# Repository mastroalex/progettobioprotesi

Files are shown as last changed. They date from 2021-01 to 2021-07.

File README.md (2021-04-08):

# progettobioprotesi
The following report aims to accurately explain what were the logical steps that led to the creation of the prototype of a rehabilitation system for the ankle. The patent provided to us was a source of inspiration for the number of components and how they relate to each other. For the shape of these we decided to deviate from the original design, opting for small variations of a mainly stylistic nature. The details and reasons for these changes will be presented below.
In this report there is also a careful study of the materials and how these can affect the functioning of the project or how they can instead bring great advantages.

---

La seguente relazione ha come obiettivo di spiegare accuratamente quali sono stati i passaggi logici che hanno portato alla creazione del prototipo di un sistema riabilitativo per la caviglia. Il brevetto fornitoci è stata fonte di ispirazione per il numero di componenti e come queste si relazionassero tra di loro. Per la forma di queste abbiamo deciso di deviare dal design originale, optando per piccole variazioni di natura principalmente stilistica. I dettagli e i motivi di queste modifiche saranno presentati più avanti.
In questa relazione è presente anche un attento studio ai materiali e come questi possano inficiare il funzionamento del progetto o come possano invece portare grandi vantaggi.

---

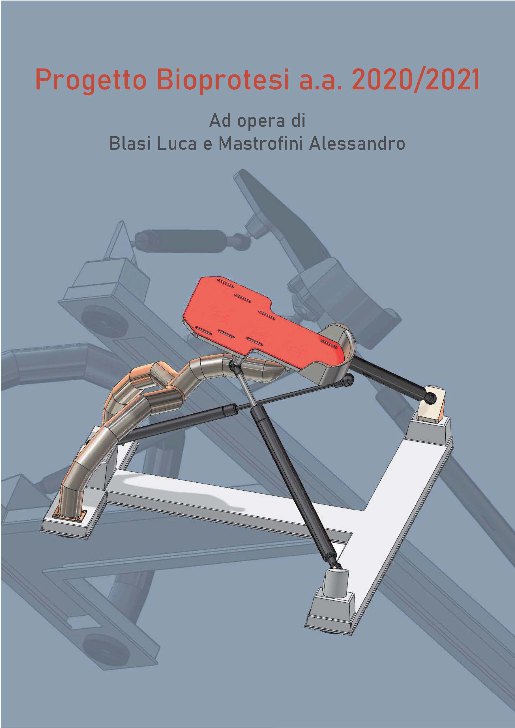
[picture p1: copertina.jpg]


## Indice 

  * [Introduzione](#introduzione)
  * [Misure e valutazioni iniziali](#misure-e-valutazioni-iniziali)
    + [Cinematica della caviglia](#cinematica-della-caviglia)
    + [Misure strumentali](#misure-strumentali)
    + [Valutazioni al calcolatore](#valutazioni-al-calcolatore)
  * [Progetto](#progetto)
    + [Considerazioni iniziali](#considerazioni-iniziali)
    + [Scelta dei pistoni](#scelta-dei-pistoni)
    + [Scelta delle dimensioni e disegno dei componenti](#scelta-delle-dimensioni-e-disegno-dei-componenti)
    + [Il giunto sferico](#il-giunto-sferico)
    + [La pedana](#la-pedana)
    + [Il braccio di supporto](#il-braccio-di-supporto)
    + [La base](#la-base)
    + [Il cappuccio (piastrina di accoppiamento)](#il-cappuccio--piastrina-di-accoppiamento-)
    + [I pistoni](#i-pistoni)
    + [Materiali](#materiali)
    + [Altri componenti](#altri-componenti)
  * [Simulazioni](#simulazioni)
    + [Flessione](#flessione)
    + [Rotazione](#rotazione)
    + [Eversione/inversione](#eversione-inversione)
    + [Pitch + roll](#pitch---roll)
    + [Un’ulteriore conferma](#un-ulteriore-conferma)
    + [Condizione di riposo](#condizione-di-riposo)
  * [Dettagli](#dettagli)
  * [Conclusioni e possibili sviluppi](#conclusioni-e-possibili-sviluppi)
  * [Materiale supplementare](#materiale-supplementare)
  * [Opere citate](#opere-citate)
  * [Indice delle figure](#indice-delle-figure)
  * [Figure extra](#figure-extra)

## Introduzione 

La seguente relazione ha come obiettivo di spiegare accuratamente quali sono stati i passaggi logici che hanno portato alla creazione del prototipo di un sistema riabilitativo per la caviglia. Il brevetto fornitoci è stata fonte di ispirazione per il numero di componenti e come queste si relazionassero tra di loro. Per la forma di queste abbiamo deciso di deviare dal design originale, optando per piccole variazioni di natura principalmente stilistica. I dettagli e i motivi di queste modifiche saranno presentati più avanti.
In questa relazione è presente anche un attento studio ai materiali e come questi possano inficiare il funzionamento del progetto o come possano invece portare grandi vantaggi.
Il brevetto US 6,277,057B1 [1] fornisce una attenta descrizione del dispositivo che riassumeremo brevemente al fine di facilitare la lettura e comprensione della relazione.
Il dispositivo si compone principalmente delle seguenti parti:
- base
- braccio di supporto 
- pedana
- apparati resistivi

La base è la componente che fornisce stabilità al dispositivo e durante l’utilizzo sarà poggiata a terra. Collegato alla base abbiamo il braccio di supporto che si estende ortogonalmente per il primo tratto dalla base per poi portarsi verso il centro di questa, ad una determinata quota dalla base. All’estremità di questo troveremo una estensione che la collega a una sfera. Quest’ultimo elemento sarà essenziale per la composizione del “ball and socket joint” che permetterà alla pedana di ruotare per creare i movimenti cardine della riabilitazione.
Sulla suddetta pedana il paziente potrà poggiare il piede la cui caviglia necessita esercizio. Al di sotto di questa pedana troviamo il socket, una cavità che permette di accogliere la sfera citata prima. Questa cavità coprirà la sfera in modo tale da bloccare le traslazioni relative tra braccio di supporto e pedana. Sarà modellata in modo tale da permettere la rotazione della sfera entro certi limiti, aspetto che discuteremo successivamente.
Questo giunto appena descritto quindi collega il braccio di supporto e la pedana, permettendone le rotazioni relative. Considerato come il braccio di supporto sia ancorato alla base sarà quindi possibile immaginare la pedana sollevata da terra e libera di ruotare.

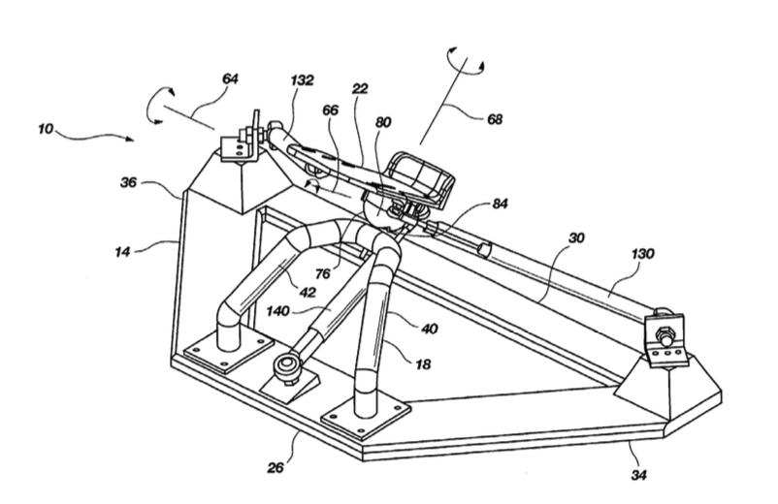
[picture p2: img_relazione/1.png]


> **Fig. 1** - Fig. 1 – Immagine tratta direttamente dal brevetto US 6,227,057B1 [1]

Alla stessa pedana sono anche collegati quelli che il brevetto definisce come “resistive means”, ossia congegni capaci di opporre resistenza ad allungamento ed accorciamento. Questi congegni collegheranno direttamente la pedana alla base, con l’obiettivo di opporre resistenza, elemento fondamentale della riabilitazione.
Facendo riferimento alle normative ISO 20957-1 per le attrezzature da allenamento e la normativa ISO 14971 per la gestione del rischio per i dispostivi medicali abbiamo cercato di focalizzaci su un dispositivo semplice e con bassi costi di produzione e manutenzione che garantisse un certo comfort all’utilizzatore ma che al contempo fosse stabile durante il movimento e riducesse al minimo la possibilità di ulteriori infortuni. Essendo un dispositivo di riabilitazione deve garantire il corretto movimento articolare in tutte le direzioni e permettere un certo lavoro tale da favorire la rigenerazione corretta dei tessuti danneggiati ma allo stesso tempo deve limitare movimenti troppo bruschi e bloccare il movimento ai limiti articolari prevenendo ulteriori infortuni [2, 3, 4, 5].
Il dispositivo, per come è stato strutturato, prevede sia un carico isometrico ai limiti articolari sia un intenso esercizio propriocettivo volto ad ottimizzare il recupero della cinematica articolare.
Una particolare attenzione è stata dedicata anche alla scelta di un materiale che risultasse quanto più possibile anallergico e resistente alla corrosione data da un eventuale pulizia e sanificazione intensiva nel caso venisse utilizzato da più utenti, come all’interno di uno studio medico.

## Misure e valutazioni iniziali 

Una prima valutazione è stata fatta cercando in letteratura un modello semplice ma sufficientemente accurato che descrivesse la cinematica della caviglia in un modo che risultasse utile allo sviluppo del progetto. 

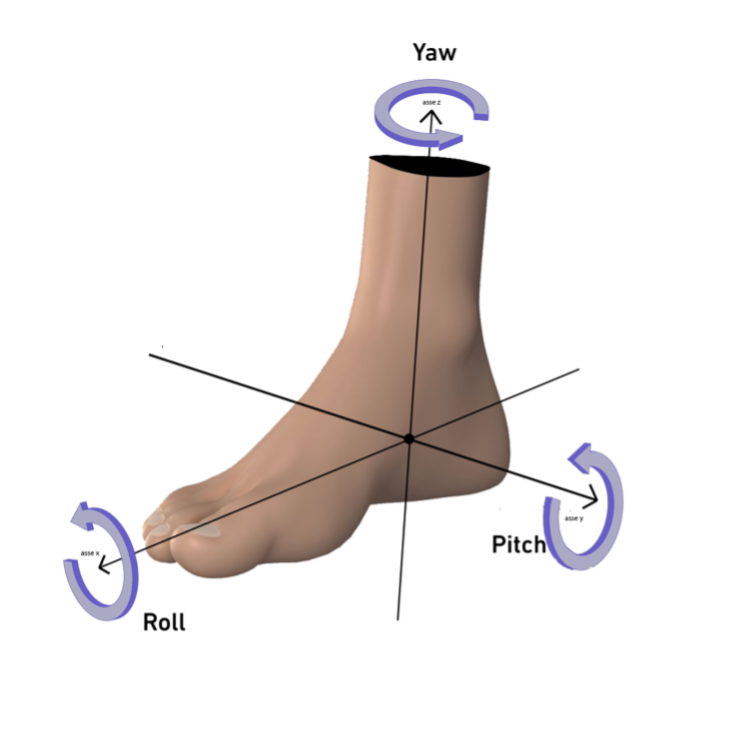
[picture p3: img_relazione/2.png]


> **Fig. 2** - Sistema di riferimento considerato per il piede destro. Le tre rotazioni sono state classificate rispettivamente come yaw (Y) intorno l’asse z, roll (R) intorno l’asse x e pitch (P) intorno l’asse y.

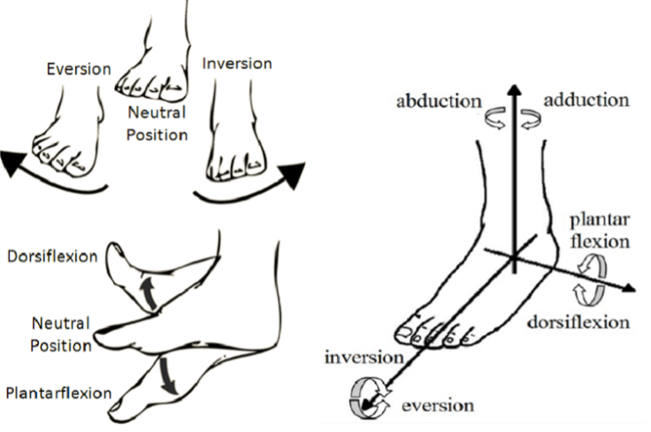
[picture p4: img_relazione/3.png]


> **Fig. 3** - Sono raffigurati i normali movimenti di rotazione dell’articolazione della caviglia. L’eversione e l’inversione indicato come (R) ovvero la rotazione intorno l’asse x. La flessione plantare e dorsale indicato come (P) ovvero la rotazione intorno l’asse y. L’abduzione e l’adduzione spesso indicate come rotazione mediale e laterale indicate come (Y) ovvero la rotazione intorno l’asse z.

### Cinematica della caviglia 

La caviglia unisce il segmento della gamba con il piede. È formata dall’unione di tre ossa: tibia, fibula e talo e da numerosi legamenti che le tengono unite e le stabilizzano. Come le altre articolazioni della gamba è responsabile del supporto del peso dell’intero corpo e richiede un’ottima rigidezza tendinea e muscolare. 

Ci sono 28 ossa e 26 articolazioni in ogni piede e caviglia che permettono un insieme di diversi movimenti e l’assorbimento della forza peso nel caso stazionario e di forze molto più intense nel caso di corsa o di impatti violenti come nei salti. Gran parte delle articolazioni sono delle anfiartrosi con legamenti molto rigidi che permettono soltanto movimenti minimi tuttavia conferiscono al piede una notevole flessibilità elastica e consentono di distribuire i carichi di compressione agenti in tensioni elastiche sui legamenti di una struttura complessivamente leggera. L’escursione del piede è variabile da persona a persona e con l’età ed è bene sottolineare il fatto che l’escursione complessiva data sia dall’articolazione talocrurale che subtalare è notevolmente maggiore della somma delle escursioni di ogni singola articolazione la ragione di tale fenomeno risiede nei legamenti il cui grado di tensione può essere aumentato o ridotto a seconda dei movimenti delle strutture adiacenti. L’articolazione talocrurale è formata dalla tibia, dalla fibula (o perone) e dalla troclea dell’astragalo e dai numerosi legamenti e capsula articolare necessari alla stabilizzazione. È un’articolazione a cerniera il cui asse decorre trasversalmente attraverso la forchetta malleolare e la troclea dell’astragalo. 

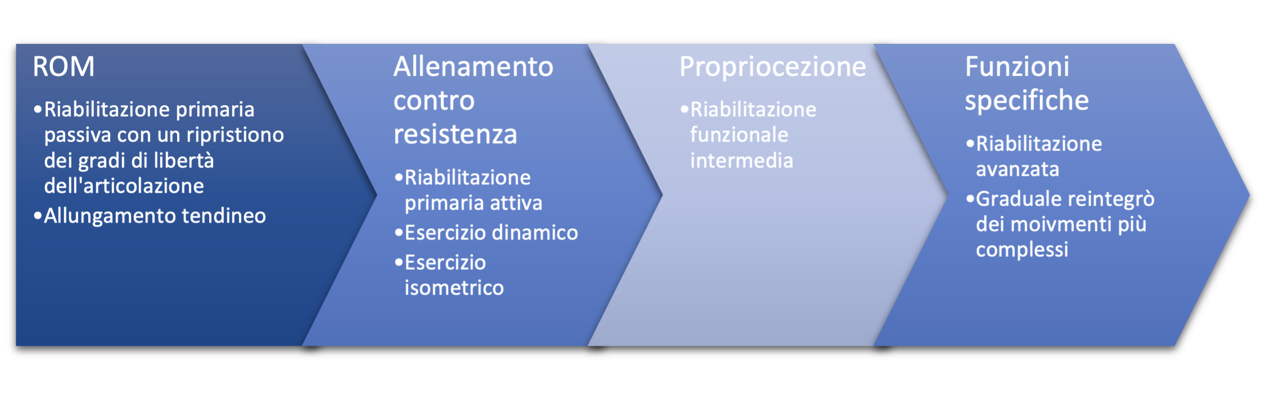
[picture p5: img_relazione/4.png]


> **Fig. 4** – Riabilitazione funzionale per la caviglia

L’articolazione subtalare è costituita da due articolazioni anatomicamente distinte ma che funzionano all’unisono permettendo una rotazione mediante un asse che decorre obliquamente attraverso il tarso. Si può distinguere un’articolazione anteriore con l’osso navicolare ed in una posteriore con il calcagno. Fig. 5 
Le due articolazioni sono strettamente collegate tra loro dal punto di vista funzionale e l’una permette di ampliare lo spazio di movimento dell’altra [6].

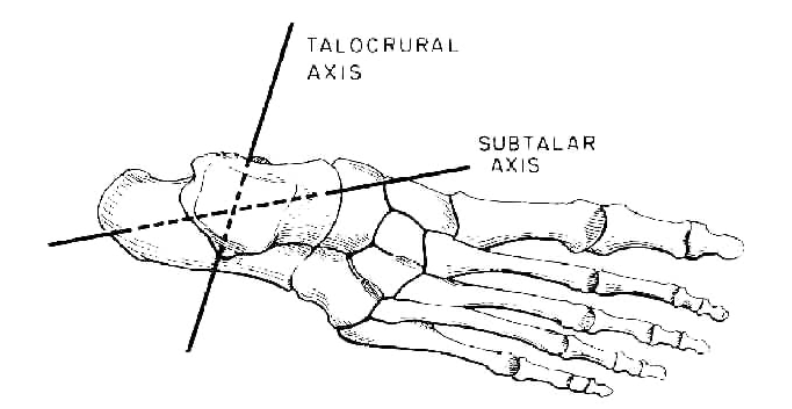
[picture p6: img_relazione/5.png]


> **Fig. 5** – Assi di rotazione delle articolazioni talocrurale e subtalare [7]

Le lesioni più comuni sono le distorsioni e al secondo posto le fratture. Mentre la frattura prevede l’interruzione della continuità ossea, la distorsione indica tutte le lesioni delle articolazioni e dei tessuti molli ad esse legati, provocati da movimenti anomali che eccedono i limiti fisiologici delle articolazioni. 

Il trattamento per queste lesioni prevede le seguenti fasi:
- Trattamento per eventuali emorragie, ghiaccio, bendaggi compressivi, antiinfiammatori 
- Inizio del recupero con una fase attiva volta a ripristinare la mobilità articolare. Inizia da 1 a 3 settimane dopo la lesione
- Inizio di movimenti complessi compresa l’attività sportiva mantenendo comunque gli esercizi di recupero.
Gli esercizi di riabilitazione per la caviglia prevedendo un basso carico, una lunga durata e una forte ripetitività dei movimenti. [8]

È importante notare come oltre a migliorare la forza e la resistenza dell’articolazione i pazienti devono anche accrescere la propriocezione garantendo una maggiore stabilità alla caviglia. Una mancanza di propriocezione porta ad una maggior debolezza articolare e quindi ad un elevato rischio di lesione pertanto è necessario prevedere una riabilitazione che considera anche questi fattori [9, 10].

In letteratura si trovano sostanzialmente tre categorie di modelli cinematici: articolazione talocrurale e subtalare rappresentati come un giunto cilindrico, la caviglia che viene rappresentata come un giunto sferico oppure la caviglia viene rappresentata come un quadrilatero articolato [11].
Una descrizione sufficientemente accurata per il progetto in questione è stata identificata nella pubblicazione di C. Brockett  [12]. Consideriamo quindi tre diversi assi di rotazione (Fig. 2) sui quali possiamo identificare una rotazione positiva ed una negativa rispetto al piano neutro. Questo ci porta ad identificare 6 rotazioni indicate in Fig. 3, tratta dalla pubblicazione di C. Racu [13]. 

È anche opportuno considerare il rapporto tra la forza 1 RM, ovvero il carico che consente una sola ripetizione di un movimento, nonché il carico massimale, e il numero di ripetizioni tipicamente possibili per una certa frazione di questo carico. Come mostrato in letteratura tipicamente lavorando al 60% del carico è possibile effettuare più di 20 ripetizioni [14, 15]. 
Inoltre, è necessario considerare che trattandosi di riabilitazione è bene rimanere distanti dal carico massimo e lavorare ad una percentuale del carico massimo molto bassa riuscendo così ad effettuare un elevato numero di ripetizioni provocando una quantità di stress sufficiente ad indurre una risposta dai tessuti danneggiati ma ben lontana sia dalla soglia di dolore che dal punto in cui potrebbero provocarsi altri danni ad un tessuto che non ha ancora recuperato del tutto le sue funzionalità.
Parlando di carico massimo in questo caso facciamo riferimento alle forze misurate ai limiti articolari in una posizione isometrica che quindi sappiamo essere tra le forze più elevate a cui può essere sottoposta l’articolazione [16], di cui parleremo più avanti.  
Mentre in una fase tardiva della riabilitazione può essere utile aumentare il carico nell’ottica di indurre un rafforzamento dell’intera articolazione.

Un altro fattore interessante è quello che avendo il dispositivo dei blocchi ai limiti articolari è anche possibile, dopo aver portato il piede al limite articolare desiderato, effettuare delle sessioni di isometria, anch’esse molto utili dal punto di vista riabilitativo. 
Questi esercizi sono comunque pensati nel rispetto di diverse linee guida ormai note in letteratura [17] ed è consigliato comunque un consulto con un fisioterapista al fine di programmare e ottimizzare le singole procedure in dettaglio.

Si è quindi reso necessario ottenere delle misure che ci permettessero di dimensionare correttamente sia i limiti articolari del dispositivo che la giusta resistenza esercitata dai pistoni

Prima di procedere alle misure ci è sembrato necessario scegliere un sistema di riferimento per rendere più chiaro e coerente tutto il progetto. Il sistema di riferimento è stato preso come una terna destra con l’asse z orientato lungo la tibia, un asse x orientato lungo le dita del piede e un asse y perpendicolare ad entrambi. (Fig. 2)

La trattazione è stata eseguita rappresentando principalmente il piede destro, tuttavia, il dispositivo può funzionare con entrambi i piedi ed è stato dimensionando considerando dei valori medi tra i due piedi e cercando di mantenere il più possibile la simmetria.

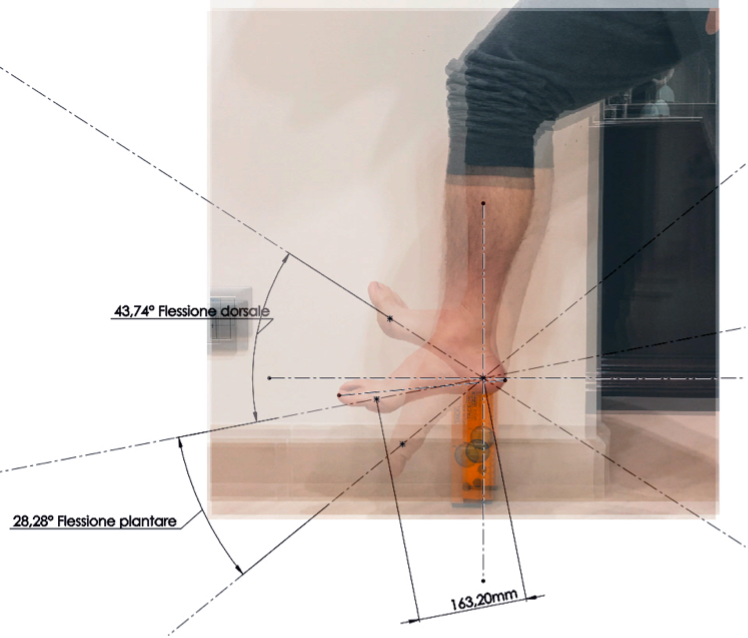
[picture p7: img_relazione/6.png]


> **Fig. 6** - Misurazione in SOLIDWORKS © delle rotazioni nel caso di flessione plantare e dorsale mediante le rette passanti per i marker. 

### Misure strumentali

Le misure sono state effettuate per entrambi i piedi.

Le prime misure rilevate sono state le dimensioni della pianta del piede destro e sinistro 25cmx9cm e successivamente sono state acquisite le immagini delle rotazioni sui tre assi considerati. Le immagini sono state acquisite con una ripresa a 60 frame al secondo da cui sono stati successivamente estratti i frame corrispondenti ai punti estremali delle rotazioni. Per rendere più precise le successive elaborazioni sono stati segnati sul piede alcuni marker con un pennarello (spiegato nel paragrafo seguente) e la ripresa è stata effettuata ponendo la camera quanto più possibile parallela al piano dove avveniva la rotazione e quanto più orizzontale possibile.

Successivamente sono state misurate le forze espresse nei punti estremali delle rotazioni per i movimenti di flessione plantare e dorsale, rotazione mediale e laterale, eversione e inversione.
Il valore è stato misurato nella direzione parallela agli assi di riferimento. 
Sono stati raccolti tre valori per ogni situazione e ne è stata presa la media tra il piede destro e il piede sinistro.
I valori sono stati raccolti mediante l’uso di un dinamometro digitale con una precisione di 10g [18] che forniva una misura di massa, quindi convertiti in forza peso.  
Il dinamometro è stato collegato al piede mediante una fascia in tessuto non elastico, un gancio e un cavo rigido Fig. 8
I valori sono raccolti in Fig. 7 e Tab. 1.

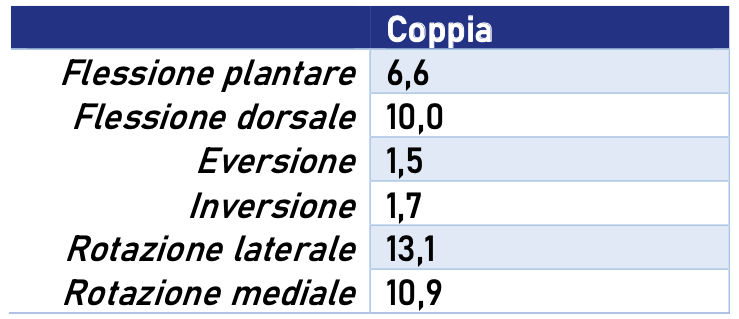
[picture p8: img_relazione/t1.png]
Tab1


> **Tab. 1** – Coppie (Nm) calcolate con la media delle forze misurate e il braccio misurato rispetto il punto dove è stata ancorata la fascia per le misure delle forze, tenendo conto della rotazione media.

Le varie misure sono state effettuate in diverse giornate e in momenti diversi della giornata al fine di stimare una media che non fosse alterata dallo stato di fatica dell’articolazione.

Per avere un’ulteriore conferma sono state effettuate delle misure anche con un inclinometro [19] al fine di avere un secondo riscontro sulle misure angolari Fig. 8. Il dispositivo è stato ancorato al piede mediante una fascia elastica che lo ha mantenuto stabile e solidale al piede. Durante i movimenti si è cercato di mantenere la pianta del piede quanto più dritta possibile cercando di evitare possibili artefatti dovuti alla curvatura del piede.

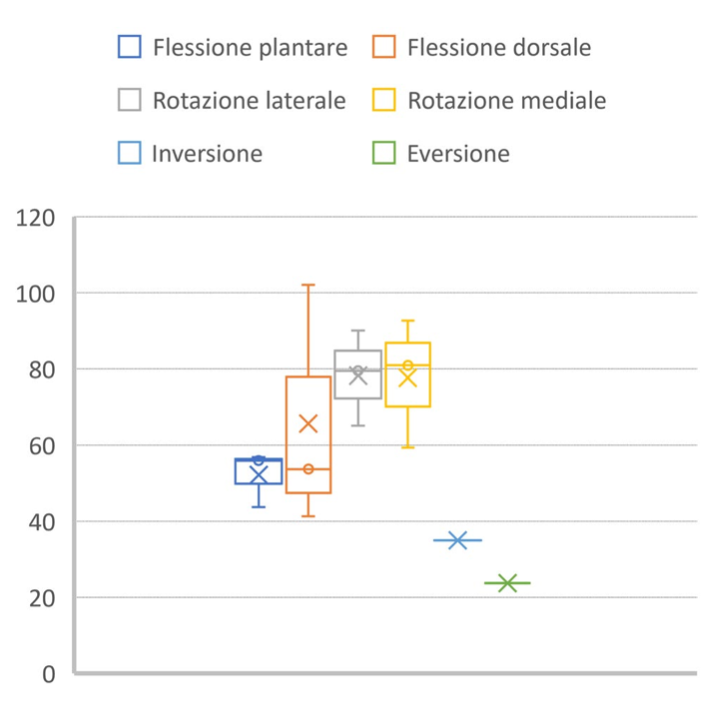
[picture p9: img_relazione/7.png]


> **Fig. 7** - Distribuzione delle misure delle forze [Newton] effettuate nelle 6 posizioni limite per entrambi i piedi. La croce evidenzia la media, valore che è stato considerato nel resto della trattazione.

### Valutazioni al calcolatore 
Successivamente sono stati elaborati i video estraendone i frame negli istanti di massima rotazione. Sui singoli frame sono stati applicati diversi filtri per rendere più marcato il contrasto sia tra il piede e lo sfondo sia tra piede e marker. I file immagine sono stati importati all’interno del software SOLIDWORKS © nell’ambiente di schizzo. 

Prima è stata importata l’immagine nella posizione neutra tracciando un segmento tra i marker e scalando l’immagine in modo tale che il piede risultasse esattamente in scala 1:1 sulla base delle misure precedentemente effettuate.
Poi sono state importate le immagini delle due rotazioni estremali e impostate in trasparenza in modo tale da vedere la posizione neutra. Nuovamente sono stati uniti i marker con un segmento. Mediante lo strumento “misura intelligente” sono state valutate le rispettive inclinazioni nei due punti estremali delle rotazioni Fig. 6. 
Lo stesso procedimento è stato effettuato per tutti e tre gli assi.
I dati risultanti sono raccolti in Tab. 2.
Quindi è stata presa la media tra piede destro e sinistro Tab. 3. 

Le approssimazioni e le imprecisioni le assumiamo trascurabili poiché stiamo affrontando un organismo biologico, per altro in una fase riabilitativa, quindi l’effettivo stato e i movimenti potrebbero cambiare di seduta in seduta e dipendere dallo stato psicologico, stress prodotto dalle sedute precedenti, risposte infiammatorie dei tessuti e tanti altri fattori che rendono accettabile un certo grado di incertezza.  

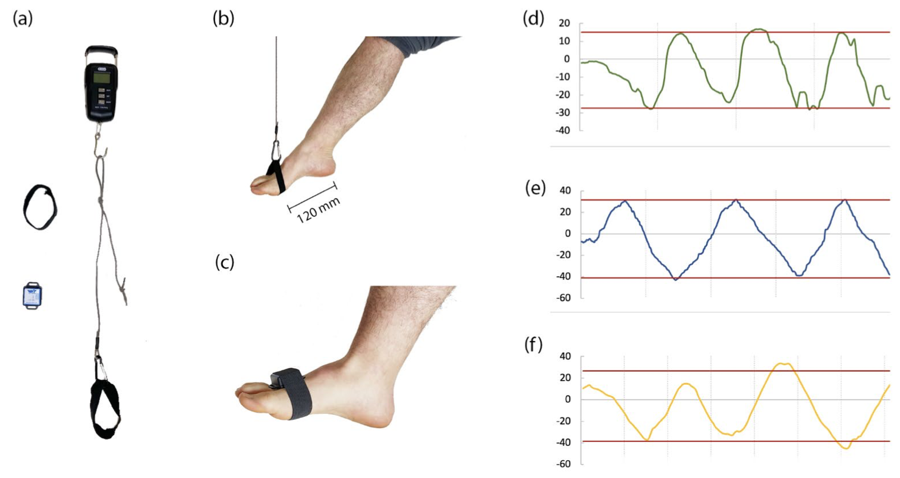
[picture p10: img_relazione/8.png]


> **Fig. 8** – Sono riportati gli strumenti di misura (a) ovvero il dinamometro, l’inclinometro, le fascette in tessuto e un cavo inestensibile. In (b) la rappresentazione generale di come sono state prese le misure, precisamente il caso di flessione plantare, con la fascetta in tessuto non estensibile utilizzata per le misure della forza e in (c) la fascetta elastica con l’inclinometro. Le misure ottenute con l’inclinometro effettuando tre rotazioni consecutive in entrambi i versi prima per inversione ed eversione (d), poi flessione plantare e dorsale (e) e infine per la rotazione mediale e laterale (f). In rosso sono rappresentati i valori massimi (e minimi) ottenuti calcolando la media tra i massimi (e minimi) ottenuti per ognuna delle tre rotazioni nei due punti estremali.

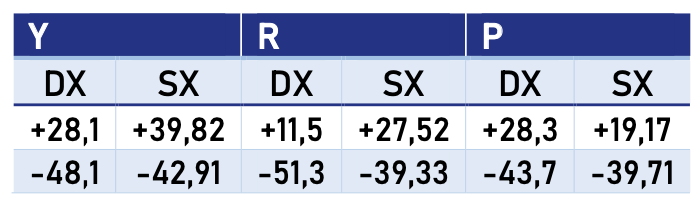
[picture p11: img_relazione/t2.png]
Tab2


> **Tab. 2** - Angoli di massima escursione misurati mediante SOLIDWORKS ©. Sono riportati i dati sia per il piede destro (DX) che sinistro (SX) per le tre rotazioni yaw (Y), roll (R) e pitch (P). I valori sono riportati in gradi e approssimati alla prima cifra decimale

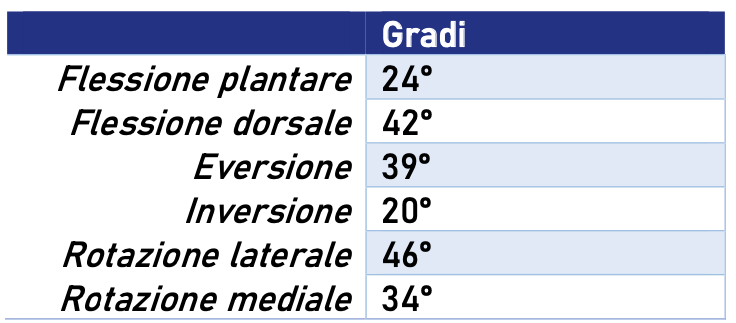
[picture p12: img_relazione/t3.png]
Tab3


> **Tab. 3** – Media approssimata dei valori di rotazione tra piede destro e sinistro. Gli angoli sono considerati in modulo, per il segno far riferimento al movimento e al sistema di riferimento.

I dati ottenuti sono stati anche controllati con diversi studi in letteratura (ROM, Pitch: 65 ÷75°, Yaw:35 ° [12]; Pitch:65÷70°, Roll:25°, Yaw:25÷30° [20]; Pitch:60°, Yaw:60° [21]; Pitch:50÷70°, Roll:50° [22]) trovando diverse corrispondenze e con le varie differenze che rientrano nella naturale variabilità biologica. 
Discorso analogo per le forze/coppie misurate.

## Progetto

### Considerazioni iniziali

Per dimensionare la pedana si è tenuto conto di diversi aspetti. 
È stato implementato un codice MATLAB © che ci permettesse di considerare la curva di carico dei pistoni e loro inclinazione per calcolare la risultante a rotazione intorno agli assi solidali alla pedana in modo da minimizzarla.
Essendo il problema con infinite soluzioni e troppe incognite per un calcolo puramente numerico sono stati considerati altri fattori come la comodità dell’utilizzatore e una dimensione complessiva tale da rendere l’oggetto abbastanza contenuto e trasportabile ma allo stesso tempo sufficientemente stabile e robusto. Queste considerazioni ci hanno fatto optare per una posizione di riposo con un’inclinazione della pedana di circa 30° e l’idea di rimanere con delle dimensioni della base non superiori ai 70cm x 50cm. Le stesse considerazioni ci hanno fatto optare per una disposizione dei pistoni laterali simmetrica e una disposizione del pistone centrale sul piano xz.
Queste considerazioni geometriche ci hanno aiutato a vincolare le escursioni dei pistoni e quindi la loro inclinazione (ulteriori considerazioni sono state fatte nei paragrafi seguenti).

### Scelta dei pistoni

Per la scelta dei pistoni abbiamo consultato il catalogo dell’azienda Stabilus © optando per la serie di molle a gas “LIFT-O-MAT” nella serie “Inox Line” in acciaio inossidabile [23].
È stata valutata l’espressione della forza in compressione/estensione riformulando quanto dichiarato dall’azienda come la legge elastica:



```tex
F\left(l\right)=F_R+F_1+\left.\frac{F_1\left(x-1\right)}{l_{max}}\right.l   (1)
```

Questa formula è stata ottenuta considerando i valori forniti da catalogo:



```tex
(F_1,\>F_R,\>l_{max},\>x=\frac{F_1}{F_2}) 
```
e considerando il caso peggiore per le valutazioni necessarie al progetto ovvero il caso di forza massima in compressione quindi considerando anche la componente FR.

Essendo una legge lineare è intuitiva la rappresentazione 



```tex
F\left(l\right)=F_1+F_R+ml
```

dove:



```tex
m=\frac{F_2-F_1}{l_{max}}=\frac{F_1\left(x-1\right)}{l_{max}}
```

e allora si ottiene la relazione (1).
Per i valori indicati si piò fare riferimento alla Fig. 9.

Per la scelta dei pistoni “Inox Line” siamo rimasti fedeli ai valori di catalogo con FR=60N, x=1,35 e per F1 un valore di partenza di 100N con incrementi di 25N. I valori di F1 vincolano anche la lunghezza di massima estensione e quindi la lunghezza massima del pistone tra i due attacchi.

Il codice MATLAB © ci ha aiutato a calcolare una disposizione dei pistoni sulla piattaforma tale da garantire un momento risultante intorno gli assi quanto più basso possibile. Qui abbiamo dovuto procedere per tentativi cercando di rispettare le considerazioni iniziali e arrivando a trovare una prima stima con i fori per i pistoni laterali ad una distanza di 65cm dalle y e una distanza di 5cm dall’asse x. Per il pistone posteriore invece una distanza di 50cm dall’asse y.
Questi valori si riferiscono ad un sistema di riferimento come indicato in Fig. 2 e con origine il centro della rotazione.

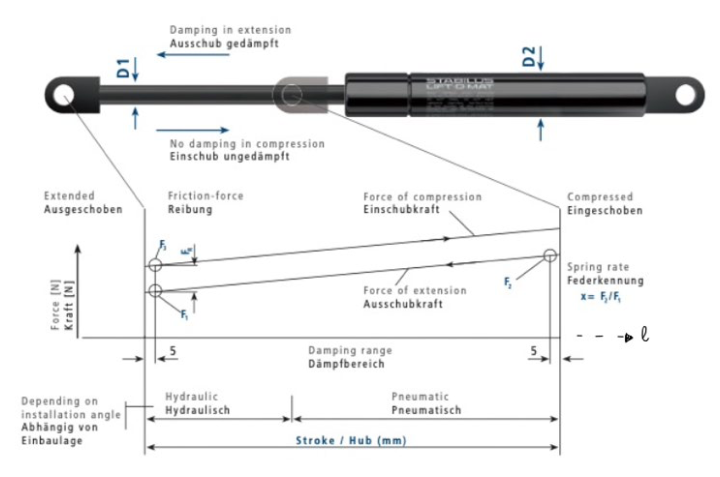
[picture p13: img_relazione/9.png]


> **Fig. 9** - Legge lineare per la molla a gas. Fare riferimento alla retta di compressione. Da catalogo vengono forniti i valori F1 ed FR, quindi è facilmente calcolabile il valore F3 (massima estensione), la pendenza ed il valore di massima compressione.  Stabilus © – LIFT-O-MAT Gas Spring.

Per il valore di forza siamo partiti da un valore di F1 = 100N per i pistoni laterale e 150N per il centrale con una compressione del 50%.

Abbiamo quindi calcolato le rigidezze risultanti e da una prima simulazione (descritta avanti) abbiamo visto come la F1 del pistone centrale risultasse troppo elevata. 
Abbiamo ripetuto quindi gli stessi passaggi scendendo fino a 100N (per il modello Inox Line si va da 100N a 600N con incrementi di 25N) ma il valore risultava ancora elevato.
Quindi siamo passati alla versione classica che ci permette di avere una F1=50N. 
Abbiamo allora ripetuto tutti i calcoli comprese le simulazioni con questi nuovi valori.

Successivamente abbiamo verificato la compressione massima fornita dal catalogo di 150mm per il centrale e di 220mm. 
Qui abbiamo condotto ulteriori verifiche di cui parliamo avanti.

### Scelta delle dimensioni e disegno dei componenti

Tramite il codice MATLAB © abbiamo ottenuto una stima dei punti di attacco, le inclinazioni e la lunghezza dei pistoni e abbiamo preparato una prima bozza in SOLIDWORKS ©, molto schematica, tale da darci una prima visualizzazione grafica della pedana e permetterci di rilevare ulteriori misure più velocemente. (Vedi Fig. 10) 

Ovviamente il salto tra i due passaggi non è stato così diretto ma più volte siamo dovuti passare da un software all’altro per ottimizzare il tutto ed arrivare ad un buon compromesso tra le dimensioni contenute ma tali da rendere stabile il dispositivo, utilizzo di pistoni simili e con valori da catalogo, comodità dell’utilizzatore. 
  
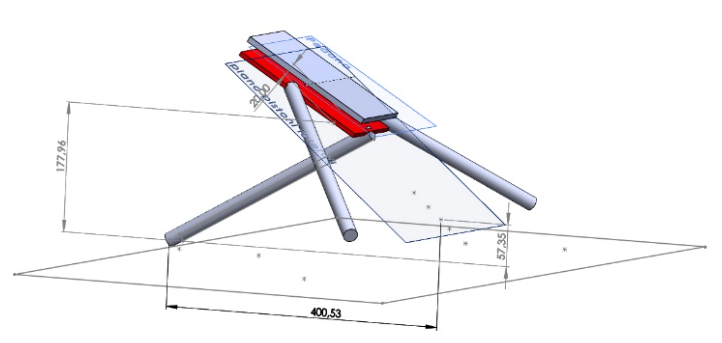
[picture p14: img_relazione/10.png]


> **Fig. 10** – Prima bozza schematica realizzata a partire dai dati ottenuti tramite il codice MATLAB © con il fine di manipolare meglio le geometrie e avere dei riferimenti più concreti.

Successivamente siamo passati ad un disegno più accurato di pedana, braccio di supporto e base in modo da valutare anche le rotazioni e poi poter passare a delle simulazioni vere e proprie.

### Il giunto sferico

Per la creazione del giunto abbiamo bisogno di diverse parti: la pedana, una sfera, un cappuccio e poi il perno che si collega al braccio di supporto. Nella pedana è previsto un foro a forma di calotta sferica che accoglierà la sfera che a sua volta sarà bloccata dal cappuccio. Dal foro modellato sul cappuccio (di cui parleremo in seguito) potremo garantire la connessione tra perno e sfera. Una volta vincolati perno e sfera il giunto sarà funzionante. Difatti la sfera è libera di ruotare (ma non di traslare) intorno al suo centro geometrico fino a quando il perno non arriva a battuta con il bordo del cappuccio modellato ad hoc. 
Ovviamente la sfera richiederà un materiale resistente come un acciaio al cromo e una superficie liscia.

### La pedana

La pedana si basa su un rettangolo di dimensioni 200x120cm tale da lasciare libere le dita e sono stati inserite delle asole per poter far passare alcune cinte per il fissaggio del piede come suggerito nel brevetto. La pedana ha uno spessore di 6mm (Fig. 11).

È stato poi aggiunto un supporto per il tallone.
Dopo le ulteriori valutazioni geometriche sono stati aggiunti 3 tacchetti su cui praticare i fori per i perni dei pistoni. I fori per i pistoni laterali sono perpendicolari alla pedana mentre per il pistone 

centrale è stato necessario inclinarlo (vedi discussione sui perni dei pistoni).  Fig. 13
 


> **Fig. 11** - Geometria di partenza per la pedana

Un’ulteriore aggiunta è stata fatta creando la sede per la sfera del giunto sferico con i fori per le viti della copertura di fissaggio. 
Sono stati poi aggiunti alcuni dettagli estetici come sformature e raccordi.
Globalmente ha un peso di 1,428 kg con un baricentro sull’asse di simmetria e spostato di 74,64 mm dal centro del giunto sferico, nella direzione del piede. 

È stata anche valutata la possibilità di asportare del materiale dalla parte inferiore al fine di renderla più leggera ma ciò non è stato necessario in quanto questo peso aggiuntivo ci consentiva di stabilizzare meglio la posizione di riposo. 

È stato anche aggiunto un foglio di materiale polimerico rigido dallo spessore di 1,5mm sulla superficie al fine di rendere più confortevole la pedana, migliorare l’adesione e limitare la sensazione di freddo provata a contatto con materiali metallici. Il materiale polimerico risulterà inoltre resistente agli attacchi chimici che un oggetto del genere può subire: chiaramente durante la vita del prodotto sarà necessario disinfettare adeguatamente la superficie, soprattutto nel caso questo oggetto sia presente in uno studio specializzato di riabilitazione. Tale superficie polimerica è pensata anche per resistere ai disinfettanti. Un possibile candidato è il polipropilene, polimero termoplastico che oltre alla bassa densità vanta una buona resistenza termica e all’abrasione, inoltre è riciclabile. 

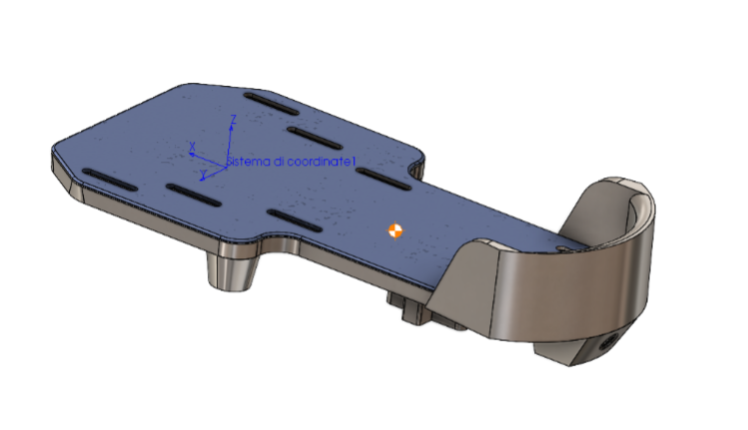
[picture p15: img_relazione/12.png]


> **Fig. 12** – Pedana completa con la copertura superficiale in materiale polimerico. Presente anche il sistema di riferimento solidale alla pedana e il centro di massa.

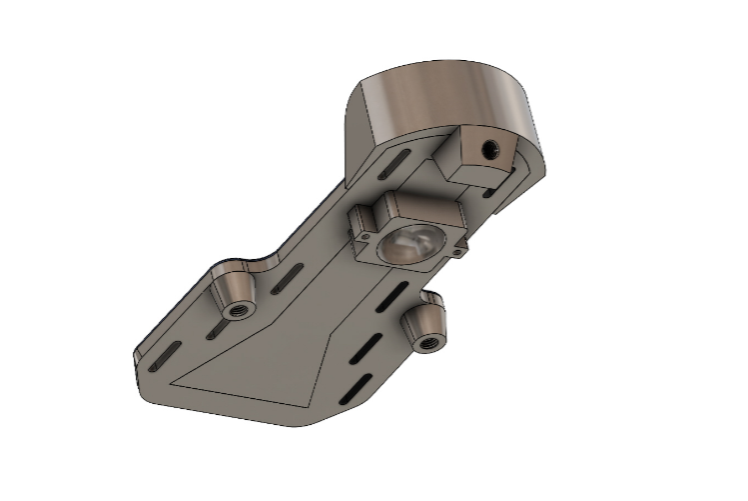
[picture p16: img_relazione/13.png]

 
> **Fig. 13** – Vista inferiore della pedana. Si vedono i tacchetti per i fori, la sede per il giunto sferico e la forma generale valutata come ipotesi per eliminare del materiale qualora fosse risultato necessario.
Infine è stata aggiunta la porzione che si collega al giunto sferico tramite una estrusione seguita da un taglio in rivoluzione per creare il foro che accoglierà la sfera. 

### Il braccio di supporto

Per la modellazione del braccio di supporto dopo vari tentativi, cercando di combinare in vario modo delle estrusioni e delle geometrie di rivoluzioni per seguire la forma fornita dal brevetto abbiamo notato che il brevetto si riferisce alla forma del braccio di supporto come “wishbone” che indica la forcula, osso presente negli uccelli. Questo ci ha fornito uno spunto per pensare a una forma meno appuntita. Ci siamo quindi affidati a delle geometrie di loft, che sicuramente creano forme più sinuose. 

Affidandoci alle misure fornitoci dal programma MATLAB © sviluppato, ragionando per simmetria, abbiamo fissato nello spazio due punti da cui abbiamo imposto una estrusione che poi si sarebbero collegate tra loro tramite le geometrie di loft (con aggiunta di vincoli di inizio e di fine per ridurre al minimo il numero di spigoli). Successivamente abbiamo introdotto un perno a cui si sarebbe collegata la sfera del giunto sferico, l’inclinazione è stata pensata da poter essere ortogonale alla pedana in condizioni di riposo. 
 
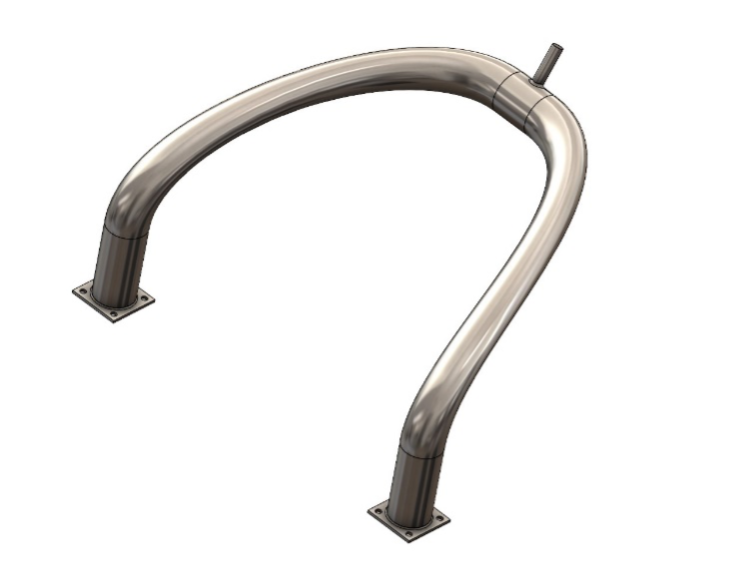
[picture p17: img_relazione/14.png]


> **Fig. 14** - Primo prototipo “wishbone” per il braccio di supporto

Questa geometria presenta un problema: la forma è tale da andare facilmente a battuta con i pistoni laterali, soprattutto nei movimenti di rotazione esterna/interna. 
Dopo diversi tentativi di rimodellamento e misurazioni ci siamo ingegnati per evitare calcoli articolati sviluppando una nuova geometria, che chiameremo “Geometria ad Y”. 
Questa versione combina la forma della forcula con la necessità di evitare il contatto tra il pezzo e i pistoni, la novità sta quindi in questa nuova estremità più longilinea che parte dal braccio per collegarsi alla pedana. 

L’ultima versione (Fig. 15) è considerata come formata da diversi segmenti cilindrici cavi cosi da diminuire il peso complessivo e fornire anche una maggiore resistenza meccanica. Inoltre questa struttura è anche più facilmente realizzabile.

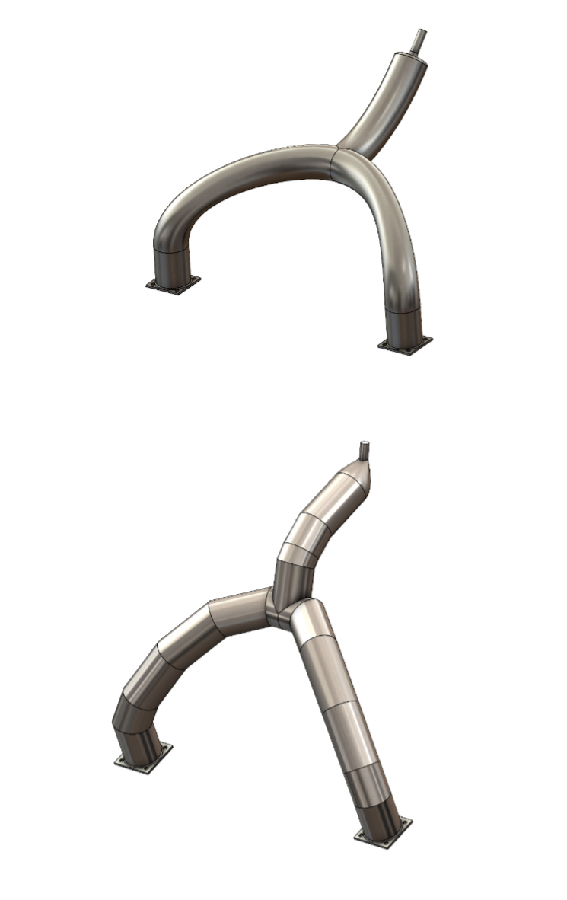
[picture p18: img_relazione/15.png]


> **Fig. 15** - I modelli di braccio di supporto “geometria ad Y”. Sopra una bozza e sotto il modello definitivo.

Alle estremità che si ancorano alla base sono state progettate delle piastre con fori per viti M4, di distanze 39x39mm. 

### La base

La base è stata probabilmente il pezzo che ha subito più modifiche dal modello originale, inoltre è sicuramente quello con più versioni. 

Abbiamo provato con la forma a trapezio forato come da modello, abbiamo provato una forma a V rovesciata e ne abbiamo pensate diverse altre. 
 
> **Fig. 16** – Foto dei primi prototipi per la base

La versione che presentiamo ha una peculiare forma ad H con braccia di diversa lunghezza, ciò permette di fornire gli stessi identici ancoraggi delle altre versioni, risparmiando in volume. Un design che risparmia in volume risparmierà in massa. 

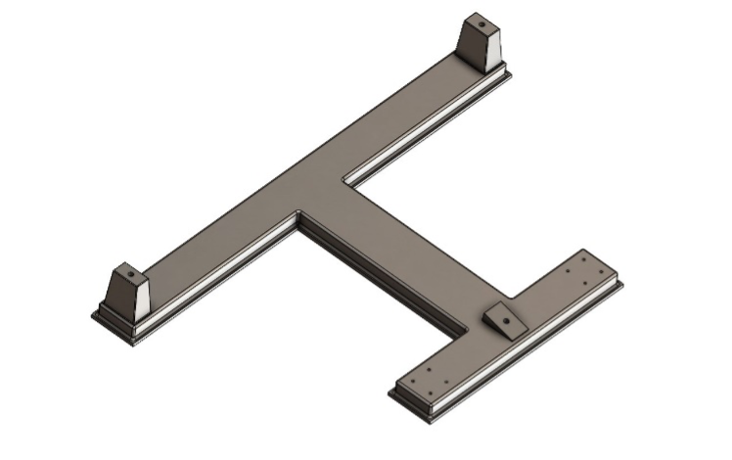
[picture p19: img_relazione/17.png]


> **Fig. 17** – Modello della base con forma ad H
Chiaramente questo aspetto diventa fondamentale nella progettazione di un dispositivo medico che può essere spostato e manovrato all’interno di un locale adibito alla riabilitazione del paziente ma anche dal paziente stesso. 

Le dimensioni dipendono dai risultati del programma da MATLAB © e dalla prima bozza che ci diranno a che distanza saranno gli ancoraggi dei pistoni e del braccio di supporto.

### Il cappuccio (piastrina di accoppiamento)

Per la creazione del cappuccio abbiamo cominciato dal creare una calotta sferica per poi aggiungere un’estrusione dal piano dove si appoggia la calotta stessa per poter applicare i fori che fisseranno il tutto alla pedana. 

In seguito abbiamo dovuto modellare il foro che avrebbe dovuto contenere il movimento della sfera e quindi di tutto il sistema. Per farlo abbiamo ripreso le misure degli angoli ai limiti articolari del piede e, immaginando la normale al piano di estrusione come la posizione del perno in condizione di riposo, abbiamo disegnato delle rette che originano nel centro di rivoluzione e formano gli angoli che forma il piede ai limiti articolari in caso di flessione e nel caso di eversione/inversione. 
Queste rette saranno gli assi dei cilindri che taglieranno la superficie della calotta, in questo modo ci è possibile di identificare visivamente la posizione del perno ai limiti articolari tramite dei fori nella calotta
Nel caso di rotazione non è stato necessario in quanto il movimento avviene intorno all’asse ortogonale alla pedana che per come abbiamo scelto la condizione di riposo si trova parallelo al perno che collega al braccio di supporto.

Successivamente, disegnata e specchiata una spline sul piano di lavoro affinché contornasse i fori citati in precedenza, abbiamo provveduto a sfruttare un taglio estruso per completare il pezzo. 

Per modellare la spline ci siamo ispirati alle immagini fornite dal brevetto che sono tali da indirizzare il piede nelle rotazioni solo degli assi principali. 
Come altra opzione abbiamo sviluppato un altro cappuccio da sostituire con la peculiarità che permette movimenti composti (e.g. flessione fino al limite articolare + eversione). 
Questa modifica potrebbe permettere una riabilitazione più differenziata per il paziente.

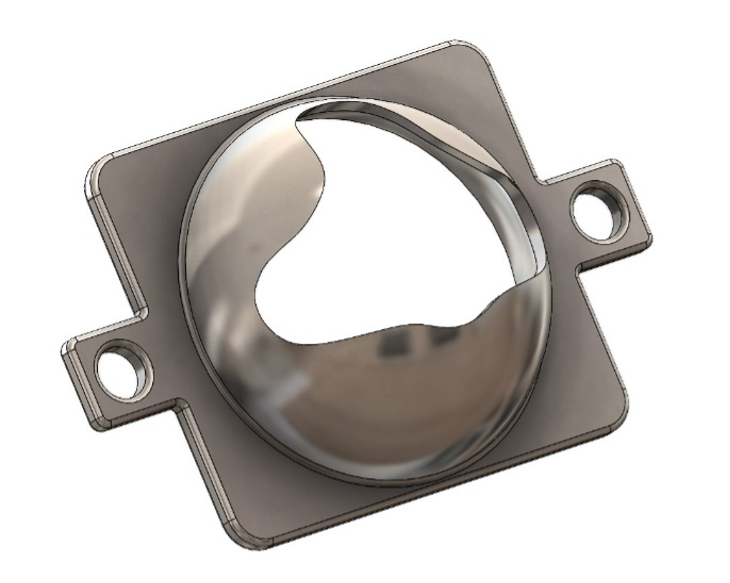
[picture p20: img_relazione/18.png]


> **Fig. 18** – Immagine del cappuccio terminata la prima modellazione

La descrizione seguente fa riferimento al progetto nella versione utilizzata per la simulazione quindi con tutti i componenti correttamente dimensionati. 

Abbiamo utilizzato gli accoppiamenti per disporre la pedana con le inclinazioni desiderate procedendo prima per il pitch, roll e yaw e poi per le combinazioni di essi ovvero pitch+roll. Questa è l’unica combinazione che abbiamo considerato poiché le altre sono meno percettibili in quanto le due articolazioni della caviglia sono tali da limitare alcuni movimenti a seconda della loro disposizione relativa.

Utilizzando quindi gli accoppiamenti per disporre correttamente la pedana in assieme abbiamo utilizzato la funzione di schizzo “curva di intersezione” per tracciare l’intersezione tra la copertura sferica e il perno di accoppiamento tra braccio di supporto e giunto sferico (Fig. 19 e Fig. 20). 
Abbiamo tracciato tutte le intersezioni per le inclinazioni di interesse, soltanto da un lato rispetto l’asse di simmetria, e poi le abbiamo proiettate su uno schizzo parallelo alla piastrina di accoppiamento. Successivamente abbiamo ottenuto una linea curva unendo questi percorsi che poi abbiamo specchiato ottenendo un percorso chiuso dal quale abbiamo fatto un’estrusione rispetto il piano (Fig. 21). 
All’estrusione abbiamo dato anche un certo grado di sformatura in modo da rendere il taglio meno netto. 
Successivamente abbiamo nuovamente verificato, per le stesse posizioni considerate per le curve di intersezione, che non vi fosse compenetrazione con lo strumento “Rilevamento interferenze”.

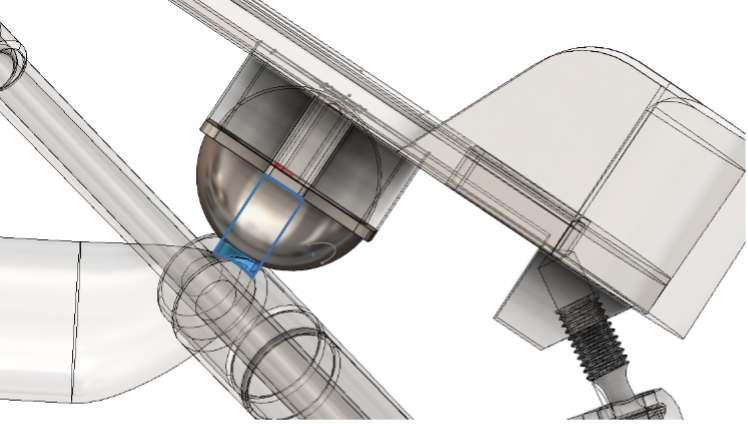
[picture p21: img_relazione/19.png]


> **Fig. 19** – Intersezione tra la copertura sferica e il perno di accoppiamento nella posizione di riposo (pedana a 30° rispetto l’orizzontale).

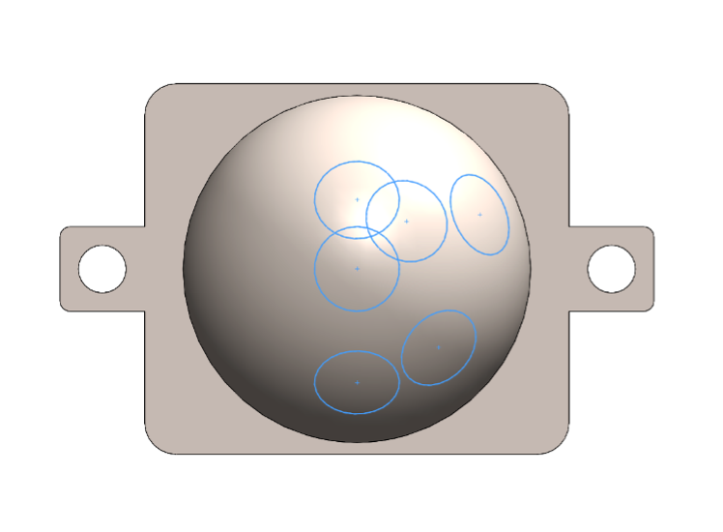
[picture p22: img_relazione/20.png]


> **Fig. 20** - Vista parallela alla piastrina di accoppiamento dello schizzo 3D delle varie curve di intersezione

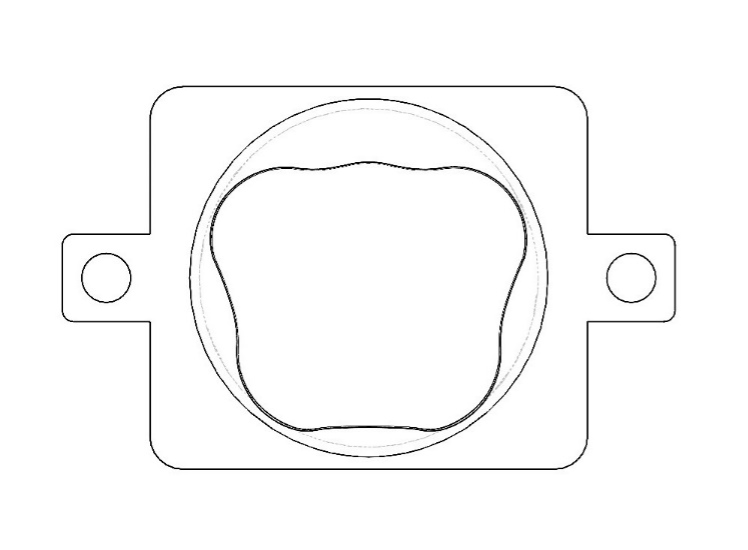
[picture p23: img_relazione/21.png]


> **Fig. 21** – Vista perpendicolare parallela alla piastrina di accoppiamento.

### I pistoni

Per i pistoni abbiamo utilizzato il file CAD fornito direttamente da Stabilus © a cui abbiamo dovuto fare alcune modifiche, sia funzionali, per permettere il corretto scorrimento tra tubo e stelo e per il giunto sferico, sia per le far sì che le dimensioni fossero esattamente quelle del catalogo (Fig. 23 e Fig. 24). 
Su questi valori abbiamo condotto diverse verifiche: per ogni movimento necessario abbiamo controllato sia che non vi fossero né una compressione né un’estensione maggiore di quella permessa. Questa verifica l’abbiamo condotta sia sulla bozza 3D (Fig. 10) che su un primo modello molto semplice (Fig. 22) tale da tener conto dell’effettivo movimento dei pistoni.
Successivamente (dopo il primo cambio tra Inox Line e la serie classica) abbiamo ripetuto le verifiche ma in una versione aggiornata dell’assieme.

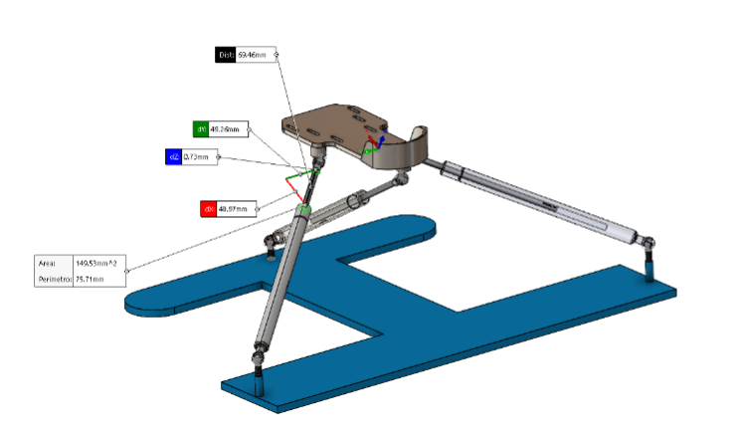
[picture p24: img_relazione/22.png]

 
> **Fig. 22** – Assieme bozza utilizzato per fare diverse misure e verifiche
Per quanto riguarda il perno con la testa sferica di diametro 10mm è stato prima ricostruito rispettando le dimensioni da catalogo, quindi considerando un perno con filettatura M8x1,25 di 13 mm e un’altezza totale di 28 mm. 

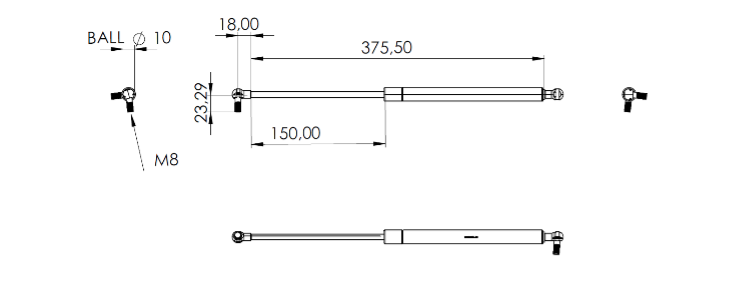
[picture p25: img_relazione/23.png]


> **Fig. 23** – Pistone centrale modificato con le misure offerte dal catalogo Stabilus ©

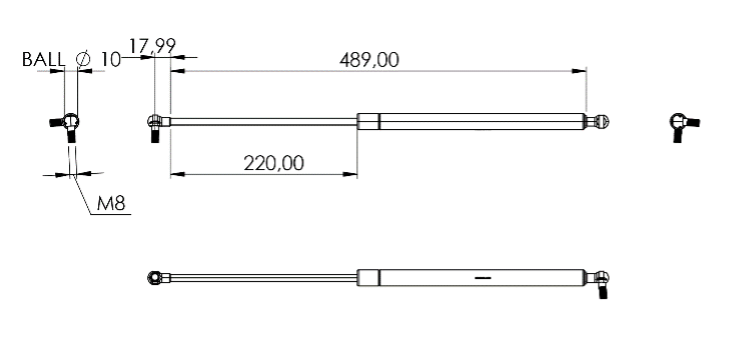
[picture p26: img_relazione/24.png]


> **Fig. 24** – Pistone laterale modificato con le misure offerte dal catalogo Stabilus ©.

I perni sono stati ripresi dopo aver completato il primo dimensionamento grossolano dei componenti per verificare consentissero effettivamente le rotazioni desiderate. 
Abbiamo utilizzato una versione quasi ultimata dell’assieme (tutti i componenti nello stato finale a meno di quale dettaglio) e il controller accoppiamenti che ci ha permesso di disporre facilmente la pedana nelle angolazioni critiche in modo da verificare con lo strumento “rileva interferenze”.
È stato allora necessario sfinare il collo prima della testa in modo da aumentare la rotazione permessa. Particolare attenzione l’abbiamo posta sul perno collegante pistoni laterali e base inclinandolo di 54° rispetto la verticale. (Fig. 25) 
Questo perno che nell’assieme utilizzato per le simulazioni risulta avvitato in realtà può ruotare liberamente (far riferimento al discorso finale). 

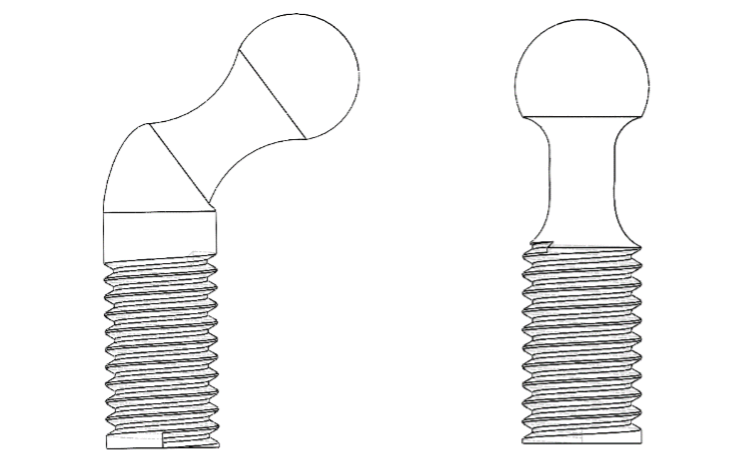
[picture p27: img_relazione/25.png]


> **Fig. 25** – Perni con testa sferica. A sinistra quello tra pistoni laterali e base e a destra quello tra i pistoni e i restanti punti di collegamento.

E bene sottolineare che nella realtà risulta permesso un pitch di 3° minore di quello ipotizzato, per entrambe le direzioni. Questa limitazione e dovuta al pistone centrale e al suo perno che non abbiamo voluto sfinare ulteriormente in modo da garantire ancora una certa resistenza (Fig. 26). 

Questo ci ha permesso di ottimizzare ulteriormente le dimensioni dei vari componenti e finalizzare alcune misure e dettagli lasciati indietro nei passaggi precedenti. 

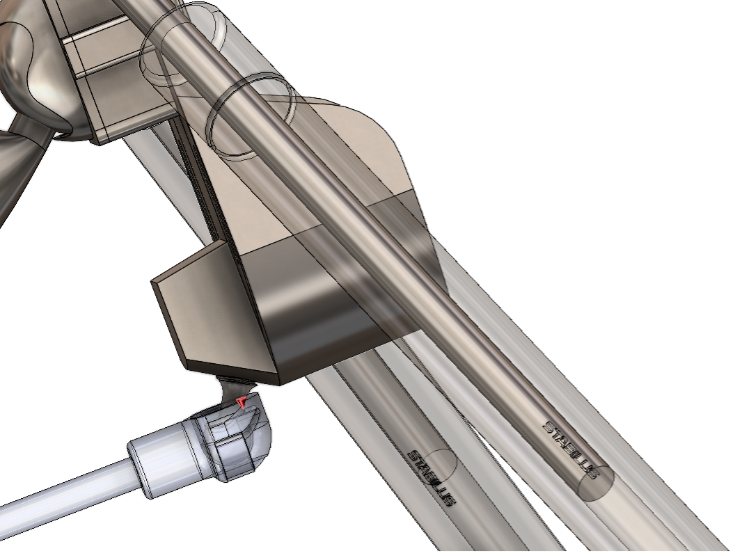
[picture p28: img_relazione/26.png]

 
> **Fig. 26** – Compenetrazione nel giunto sferico a seguito di una flessione dorsale di 42° (valore massimo)

### Materiali
Per il progetto è stato utilizzato un acciaio inossidabile AISI 316L [24] tale da mantenere la resistenza sia meccanica sia alla corrosione e tale da permettere una corretta sanificazione e pulizia del dispositivo. Questo acciaio presenta un’ottima scelta tra le ottime caratteristiche che ne fanno un materiale di punta del settore medicale e un costo relativamente basso.
Tuttavia, per un ulteriore risparmio si potrebbe utilizzare anche l’AISI 304L con caratteristiche simili ma un costo più contenuto [25, 26].

In ogni caso risulta più che appropriato un qualunque acciaio inossidabile di grado chirurgico [27, 28]. 

I pistoni sono rappresentati in acciaio inossidabile 316L e metallo con una copertura in plastica come indicato nel catalogo.

### Altri componenti

Per il fissaggio del braccio di supporto sulla base sono state utilizzate delle viti M4 a testa svasata piana con cava esagonale mentre per il fissaggio della piastrina di accoppiamento delle viti M4 con testa a bottone a cava esagonale.

Le restanti filettature sono M8x1,25 

Sono state effettuate anche delle modifiche ulteriori sulla base ed alcuni elementi collegati ad essa di cui parliamo più avanti. 

## Simulazioni

Le simulazioni sono state effettuate mediante il pacchetto aggiuntivo “SOLIDWORKS MOTION”.
È stata considerata la gravità terrestre e i componenti costituiti in acciaio AISI 316L.
È stato considerato il peso agente della gamba poggiata sulla pedana come una forza pari a 58,.86 N (misura sperimentale) applicata a 30mm dall’origine nel piano xy lungo la simmetria.
Le simulazioni hanno tutte una durata di 5 secondi.
Abbiamo considerato il contatto (steel dry- steel dry) tra piastrina di accoppiamento e il perno del braccio di supporto. Non sono state considerate le coppie sferiche di pistoni e perni in quanto avevamo già effettuato una verifica delle possibili angolazioni e di compenetrazioni ai limiti articolari, quindi abbiamo lasciato solamente l’accoppiamento di concentricità.
Il comportamento dei pistoni è stato modellato in simulazione considerando una fo𝑅𝑅rza sulla superficie dello stelo pari a F1 + FR e una molla elastica di costante adeguata e un coefficiente di smorzamento pari a 1 N/mm s. (Fig. 27 e Fig. 28)
16
 
La costante elastica è stata ricavata mediante il già citato codice MATLAB ©, ovvero 136.36 N/m per i pistoni laterali e 166.66 N/m per il pistone centrale (questo valore è quello a cui siamo arrivati dopo le considerazioni seguenti).
Una prima simulazione è stata effettuata nella condizione di riposo e ci ha portato a identificare un problema nei pistoni che ci ha costretto a passare dalla serie Inox Line alla serie classica poiché risultava necessaria una forza F1 inferiore per il pistone centrale. Questa simulazione è stata eseguita con la stessa logica delle seguenti ma lo spostamento risultava fortemente vincolato alla resistenza del pistone centrale.
Quindi abbiamo abbassato il valore di F1 a 50N arrivando così al modello finale utilizzato per le simulazioni e gli ulteriori controlli per accoppiamenti e compenetrazioni.
Lo scopo di queste simulazioni è quello di verificare che le forze/coppie necessarie per portare la piattaforma ai limiti articolari fossero ben lontane dai carichi massimi misurati e che quindi consentissero un corretto uso riabilitativo del dispositivo nel rispetto delle considerazioni fatte nel trattare la cinematica della caviglia, allora abbiamo considerato i movimenti in

### Flessione

Per la rotazione di pitch è stato imposto un accoppiamento di coincidenza tra il piano sagittale della pedana e il piano xy dell’assieme tale da bloccare le altre due rotazioni.
Questa considerazione ci è sembrata opportuna viste le condizioni di simmetria ed è stata utile per limitare problemi dovuti al solutore nel caso in cui la pedana deviasse leggermente dalla posizione esattamente centrale, situazione che nella realtà verrebbe bilanciata da un minimo lavoro del piede.
Abbiamo quindi diviso la flessione in plantare e dorsale.
Per la flessione plantare abbiamo applicato una forza pari a 55,35 N, perpendicolare alla pedana, sul piano di simmetria e a 120mm dall’origine.
Dalla simulazione è risultato uno spostamento massimo di 23° che rientra nei limiti misurati (Fig. 29).

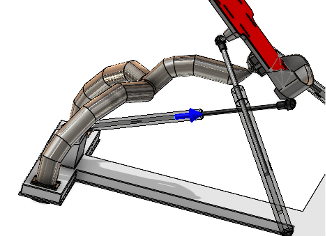
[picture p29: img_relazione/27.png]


> **Fig. 27** – Somma di F1 ed FR sul pistone centrale in fase di simulazione

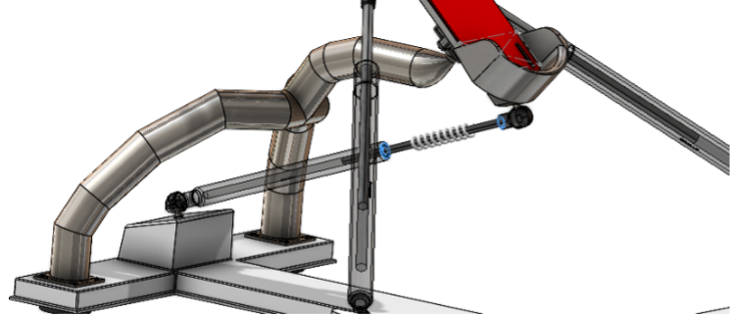
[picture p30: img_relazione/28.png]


> **Fig. 28** – Molla elastica sul pistone centrale in fase di simulazione

Tutte le simulazioni citate sono state effettuate più volte tra le varie versioni di assieme ma i risultati seguenti fanno riferimento al modello finale.

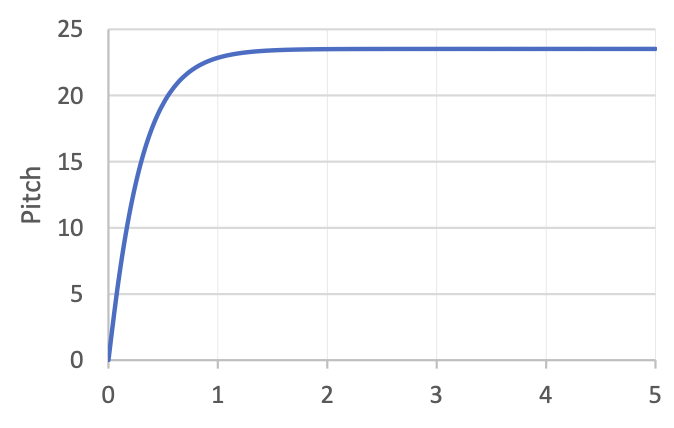
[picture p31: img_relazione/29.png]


> **Fig. 29** – Angolo di Pitch per la flessione plantare

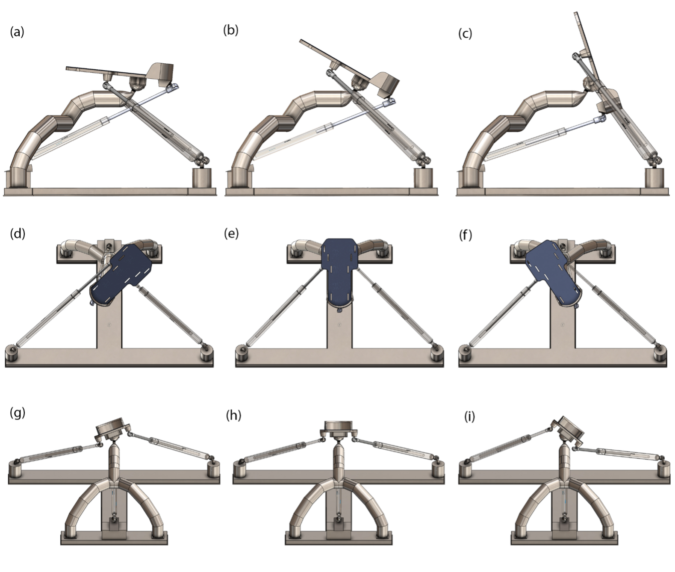
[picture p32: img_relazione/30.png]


> **Fig. 30** – In figura è riportato l’assieme principale utilizzato per le simulazioni (con meno dettagli della bozza finale). Nella colonna centrale le posizioni di riposo e nelle colonne laterali le posizioni ai limiti articolari.
 
Per la flessione dorsale è stata imposta una forza di 83,63 N, applicata nello stesso punto ma nella direzione opposta.
Dalla simulazione risulta un angolo massimo di inclinazione di 42° (Fig. 31).

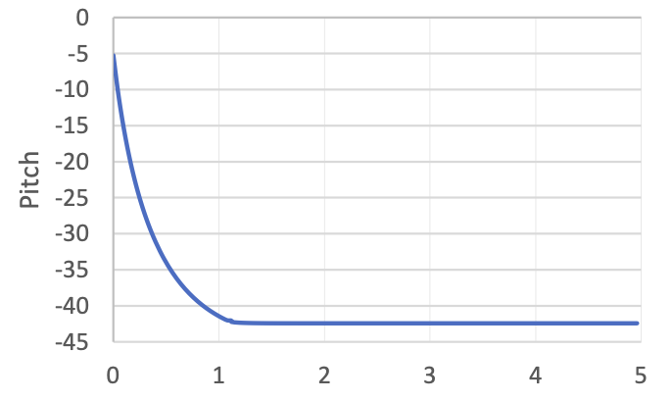
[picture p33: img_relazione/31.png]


> **Fig. 31** – Angolo di pitch per la flessione dorsale

### Rotazione
Per la rotazione abbiamo considerato la piattaforma vincolata al piano xy (inclinazione di 30° rispetto il telaio, quindi situazione di riposo).
Per la rotazione abbiamo considerato entrambi i casi e già la forza minore ci portava al limite articolare.
Quindi la simulazione seguente è stata effettuata con una forza di 90,59 N applicata nello stesso punto della flessione ma con direzione parallela ad y.
La simulazione ha quindi restituito un angolo di 63° (Fig. 32).

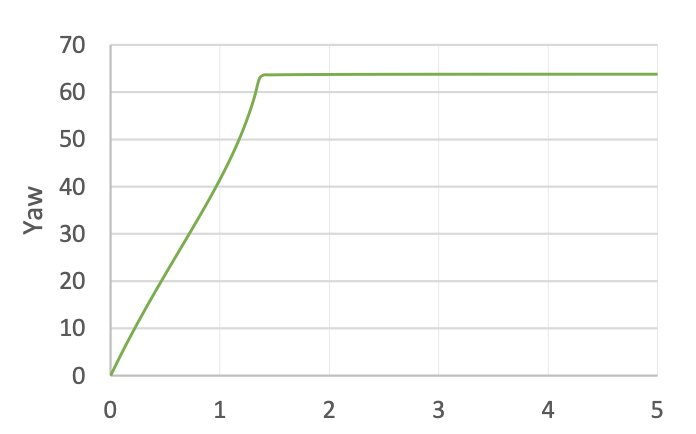
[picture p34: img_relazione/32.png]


> **Fig. 31** – Fig. 32 – Angolo di yaw per la rotazione

### Eversione/inversione 

Abbiamo considerato la pedana vincolata al piano coronale per considerazioni già fatte.
Anche per questo movimento abbiamo visto come la forza minore fosse sufficiente ad arrivare al limite articolare quindi la simulazione seguente è stata effettuata con una forza di 33,45 N applicata sul piano della pedana ad una distanza di 120mm dall’asse y e a 45mm dall’asse x. 
Abbiamo quindi verificato un’inclinazione di 41° (Fig. 33).  
 
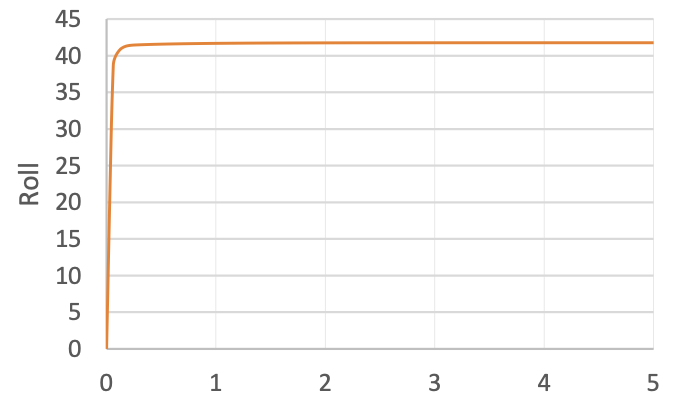
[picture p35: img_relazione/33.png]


> **Fig. 33** – Angolo di roll per l’eversione

Sulla base di questi risultati e delle misure sperimentali possiamo dire che il dispositivo permette al piede di arrivare correttamente ai limiti articolari per i movimenti cercati.

Al fine di ottenere un ulteriore riscontro abbiamo effettuato altre simulazioni.

### Pitch + roll

Abbiamo considerato un ulteriore movimento composto da una eversione/inversione e una flessione plantare (Fig. 34) e dorsale (non riportato nella relazione).
Ci è sembrato opportuno considerare questo movimento in quanto se il piede si muove lungo il piano sagittale il rapporto tra l’articolazione talocrurale e subtalare è tale da permettere movimenti più ampi rispetto la condizione di partenza. 

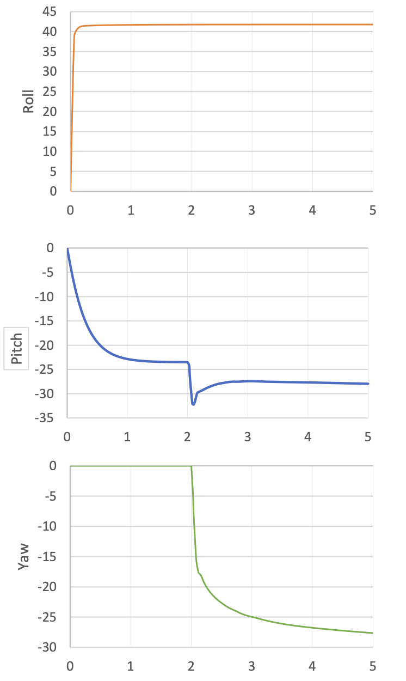
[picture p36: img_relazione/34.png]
 

> **Fig. 34** – Angoli di rotazione per pitch + roll

### Un’ulteriore conferma

Abbiamo fatto un’ulteriore prova invertendo il ragionamento: abbiamo imposto gli angoli e misurato la coppia necessaria a produrre un tale spostamento (da Fig. 35 a Fig. 38)

 I grafici seguenti esprimono la coppia in Nm.

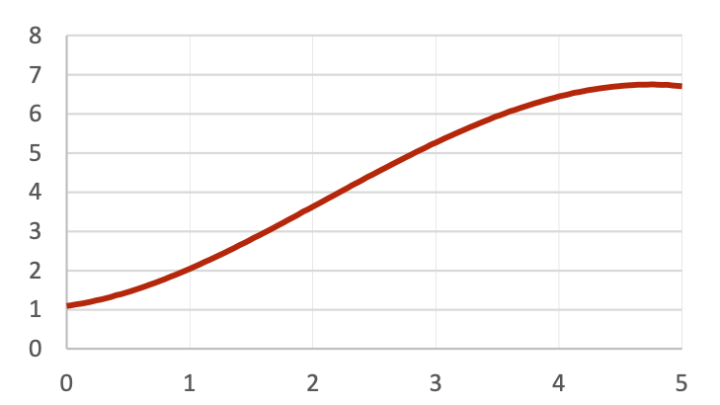
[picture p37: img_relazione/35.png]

 
> **Fig. 35** – Coppia del motore necessaria ad imporre uno spostamento di flessione plantare pari a quello misurato sperimentalmente

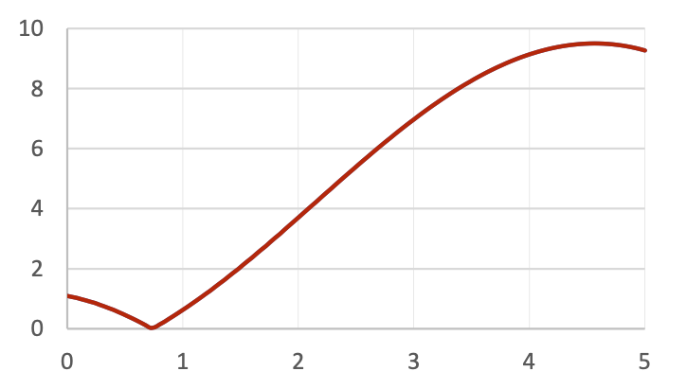
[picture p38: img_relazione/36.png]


> **Fig. 36** - Coppia del motore necessaria ad imporre uno spostamento di flessione dorsale pari a quello misurato sperimentalmente

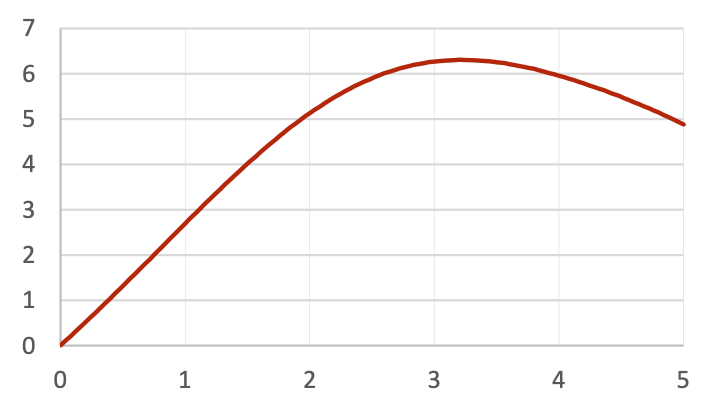
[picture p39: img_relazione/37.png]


> **Fig. 37** - Coppia del motore necessaria ad imporre uno spostamento di yaw pari a quello misurato sperimentalmente
 
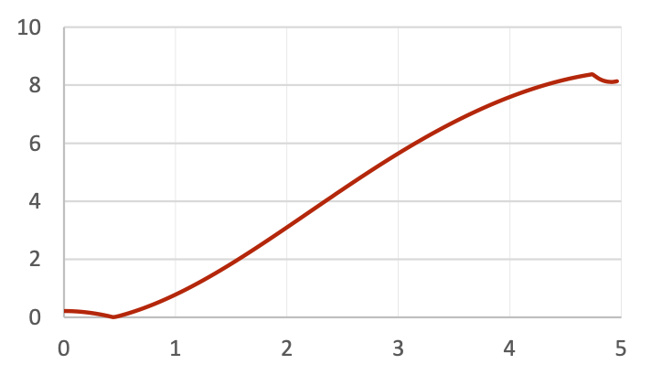
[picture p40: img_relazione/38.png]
 

> **Fig. 38** - Coppia del motore necessaria ad imporre uno spostamento di roll pari a quello misurato sperimentalmente
Spostamento per punti

Avendo già i dati dell’’inclinometro abbiamo fatto ulteriori simulazioni considerando sempre un motore ma con spostamento definito per punti. 
Anche qui abbiamo considerato due classi diverse. 

Una prima classe di controllo l’abbiamo ottenuta imponendo uno spostamento per punti con il seguente schema: riposo -> massimo -> riposo -> massimo (direzione opposta) -> riposo.

Per la seconda classe abbiamo invece considerato i dati sperimentali dell’inclinometro selezionando i valori in modo tale da avere 50 punti su 5 secondi di simulazione. 

I punti sono stati interpolati con l’interpolazione lineare. 

Entrambe le classi le abbiamo simulate per tutte e tre le rotazioni. 


 
> **Fig. 39** – Coppia simulata del motore per la classe 1
 
 

> **Fig. 40** – Spostamento imposto dal motore per la classe 1


 
> **Fig. 41** - Coppia simulata del motore per la classe 2
 
 

> **Fig. 42** - Spostamento imposto dal motore per la classe 2

### Condizione di riposo

Oltre le varie e ripetute simulazioni utilizzate per ottimizzare il dimensionamento dei pistoni abbiamo ripetuto una prova nella condizione di riposo (pedana a 30° rispetto il terreno) anche nell’assieme finale utilizzato per la presentazione. 
Anche qui i risultati mostrano soltanto una leggerissima deviazione dalla posizione ipotizzata.

## Dettagli

Particolare attenzione è stata posta anche nel rifinire alcuni dettagli estetici e funzionali.

Si può notare come in corrispondenza di diversi punti del modello siano presenti degli accordi che creano una continuità più piacevole agli occhi rispetto al classico spigolo vivo. Inoltre questa riduzione del numero di spigoli vivi è anche un vantaggio del materiale usato in quanto questi spigoli possono facilitare l’insorgere dei processi di frattura soprattutto in condizioni di carico ciclico come nel nostro modello. 

Nella fase finale del progetto è stata modificata in maniera significativa la base: 
tramite dei processi di estrusione abbiamo rimodellato l’interno della base affinché alcune parti fossero svuotate (in modo tale da alleggerire il pezzo), mentre altre risultassero piene, così da garantire solidità dove necessario, ad esempio in corrispondenza della serie di fori che accolgono le viti che stringono il braccio di supporto. 
In tal modo il prototipo richiama una lamiera spessa 3 mm formata propriamente. 

 

> **Fig. 43** – Vista in sezione del modello finale della base

Un’altra innovazione relativa alla base è stata la modifica degli ancoraggi dei pistoni laterali alla base stessa. Il sistema di semplice inserzione della vite nella base può risultare efficacie in ambiente CAD per le prime simulazioni, però nella realtà tale sistema risulta inadeguato. Per sopperire a questa mancanza abbiamo fatto della base un assieme più complesso: in corrispondenza degli ancoraggi abbiamo sviluppato un sistema costituito da un terminale collegato con cuscinetto a sfera libero di ruotare. 
Il cuscinetto è quindi da considerarsi incastrato nel foro circolare cioè solidale alla base.
Inoltre, i fori sono stati inclinati in modo tale da favorire il gioco tra perno di ancoraggio e pistone. Il sistema descritto è riportato in Fig. 44 e Fig. 45. 

Per concludere, abbiamo progettato anche dei gommini che si trovano al di sotto della base: essendo in gomma questi permetteranno alla base di rimane salda durante la sessione di riabilitazione, ma eviteranno il contatto diretto della base con il pavimento. 
Per questi ci siamo ispirati alla forma caratteristica che hanno alcune estremità di stampelle: tramite una geometria di rivoluzione abbiamo creato una serie di cerchi concentrici che mimassero la forma dei gommini delle stampelle, che risultano particolarmente efficaci. (Fig. 49)

 

> **Fig. 44** – Vista in trasparenza del sistema di ancoraggio per i pistoni laterali con un cuscinetto a sfera

 

> **Fig. 45** - Vista in sezione del sistema di ancoraggio per i pistoni laterali con un cuscinetto a sfera

## Conclusioni e possibili sviluppi

Dalle simulazioni è risultato che la forza esplicata dal piede è sufficiente a portare la piattaforma ai limiti articolari.

Il dispositivo è molto semplice e di dimensioni contenute, questo permette un utilizzo comodo sia in ambito domestico che all’interno di una clinica. 

Il dispositivo rispetta la maggior parte delle linee guida per la riabilitazione e non eccede mettendo al primo posto la salute e del paziente eliminando la possibilità di produrre ulteriori infortuni. 

Un possibile miglioramento potrebbe essere quello di utilizzare dei pistoni con attuatore che consentono di incrementare il carico passando da una prima fase di vera e propria riabilitazione fino ad arrivare ad un potenziamento vero e proprio dell’articolazione. Inoltre, questo permetterebbe di personalizzare ulteriormente il dispositivo per il singolo paziente ma renderebbe il tutto più costo e più difficile da utilizzare.

Inoltre è possibile osservare che il cappuccio risulta personalizzato sulla base dei limiti articolari del soggetto. Si potrebbe pensare di realizzare un cappuccio più permissivo e una mascherina aggiuntiva personalizzata per ogni singolo paziente e applicabile esternamente al cappuccio. 

Si potrebbero anche realizzare alcuni componenti in leghe più leggere al fine di limitarne il peso ma si rischia di incorrere in un innalzamento dei costi cercando di mantenere la stessa resistenza e stabilità. 

## Materiale supplementare

A fine documento sono riportate delle immagini aggiuntive del modello finale completo di tutte le considerazioni fatte.

Nel materiale extra troviamo:
-	Modello finale CAD nella cartella “Modello”
-	Tutte le immagini inserite
-	File di considerazioni sui pistoni estratto dal catalogo
-	Brevetto citato
-	Catalogo di riferimento
-	Dati delle simulazioni sia in file .csv che il foglio di lavoro
-	Simulazione finale su cui abbiamo effettuato tutti i test principali (simulazione 5)
-	Vecchie versioni di progetto e/o simulazione nella cartella “Old”
-	Bozza 3D di lavoro e codice MATLAB citati
-	Dati grezzi e fogli di lavoro per l’inclinometro
-	Foglio di lavoro con le forze misurate
-	File di lavoro per la misura delle rotazioni
-	Registra schermo delle simulazioni così da includere movimento e grafici

## Opere citate

- [1] 	Hayden, «Ankle rehabilitation device - US Patent 6,277,057B1,» 2001.

- [2] 	L. Chinn, «Rehabilitation of Ankle and Foot Injuries in Athletes,» Clinics in Sports Medicine, vol. 29, n. 1, pp. 157-167, 2010. 

- [3] 	Y.-N. Wu, «Combined Passive Stretching and Active Movement Rehabilitation of Lower-Limb Impairments in Children With Cerebral Palsy Using a Portable Robot,» [Online]. Available: https://doi.org/10.1177%2F1545968310388666.

- [4] 	J. E. Deutsch, «Post-Stroke Rehabilitation with the Rutgers Ankle System,» [Online]. Available: https://doi.org/10.1162/1054746011470262.

- [5] 	C. E. Syrseloudis, «Design of a Simple and Modular 2-DOF Ankle Physiotherapy Device Relying on a Hybrid Serial-Parallel Robotic Architecture,» Applied Bionics and Biomechanics , vol. 8, 2011. 

- [6] 	J. Weineck, «Anatomia sportiva,» in Principi di anatomia funzionale dello sport, Calzetti editori, 2003, pp. 181-193.

- [7] 	D. Thompson, «Ankle (talocrural) joint,» [Online]. Available: https://ouhsc.edu/bserdac/dthompso/web/namics/ankle.htm.

- [8] 	I. D. C. Racu, «An Overview on Ankle Rehabilitation Devices,» Advanced Materials Research, vol. 1036, pp. 781-786, 2014. 

- [9] 	W. R. Frontera, «Proprioception and Coordination,» in Rehabilitation of Sports Injuries: Scientific Basis, Blackwell Publishing, 2003, pp. 274-287.

- [10] 	J. S. a. Z. T. a. N. C. Dai, «cite-key Sprained Ankle Physiotherapy Based Mechanism Synthesis and Stiffness Analysis of a Robotic Rehabilitation Device,» Autonomous Robots, vol. 16, n. 2, pp. 207--218, 2004. 

- [11] 	G. F. Harris, in Foot and Ankle Motion Analysis: Clinical Treatment and Technology (Biomedical Engineering), pp. 23-25, 473-487.

- [12] 	C. L. Brockett, «Biomechanics of the ankle,» Orthop Trauma. , vol. Jun; 30(3), p. 232–238, 2016 . 

- [13] 	C. Racu, «Preliminary mathematical model of a new anklòe rehabilitation device,» Journal of Engineering Studies and Research, vol. 21, n. 2, pp. 78-84, 2015. 

- [14] 	T. Shimano, «Relationship between the number of repetitions and selected percentages of one repetition maximum in free weight exercise in trained and untrained men,» Journal of Strength and Conditioning Research, vol. 20(4), p. 819–823, 2006. 

- [15] 	E. Moraes, «Relationship between Repetitions and Selected Percentage of One Repetition Maximum in Trained and Untrained Adolescent Subjects,» Journal of Exercise Physiology, vol. 17, n. 2, 2014. 

- [16] 	W. S. Doss, «A comparison of concentric, eccentric, and isometric strength of elbow flexors». 

- [17] 	C. G. Mattacola, «Rehabilitation of the Ankle After Acute Sprain or Chronic Instability,» Journal of Athletic Training , vol. 37, n. 4, p. 413–429, 2002. 

- [18] 	«PS01 Electronic Balance Digital Fishing,» Dr. Meter, [Online]. Available: https://www.amazon.it/gp/product/B078KP5YGP/ref=ppx_yo_dt_b_search_asin_title?ie=UTF8&psc=1.

- [19] 	Witmotion, «BWT901CL - 9 Axis IMU Sensor Angle Inclinometer + Acceleration + Gyro + Mag,» [Online]. Available: https://www.wit-motion.com/bluetooth-gyroscope/witmotion-bluetooth-2-0-mult-connect-bwt901cl-9-axis.html.

- [20] 	M. J. Girone, «Rutgers Ankle orthopedic rehabilitation interface,» 1999. 

- [21] 	J. Yoon, «Reconfigurable ankle rehabilitation robot for various exercises,» Journal of Robotic Systems, vol. 22, n. S1, pp. S15-S33, 2006. 

- [22] 	A. Logan, «The foot and the ankle - Clinical Applications,» pp. 35-50.

- [23] 	Stabilus, «LIFT-O-MAT Gas Spring,» [Online]. Available: https://www.stabilus.com/products/non-locking-gas-springs .

- [24] 	Carpenter technology, «Biodur ® 316LS,» [Online]. Available: https://www.carpentertechnology.com/alloy-finder/Biodur-316LS.

- [25] 	AZO Material, «Medical Applications of Stainless Steel 304 (UNS S30400),» [Online]. Available: https://www.azom.com/article.aspx?ArticleID=6641.

- [26] 	MEPS International Ltd, «World Stainless Steel Price,» [Online]. Available: https://worldsteelprices.com/stainless-steel-prices/.

- [27] 	N. M. Winters GL, Stainless Steels for Medical and Surgical Applications, 2003. 

- [28] 	Y. Murty, «Use of stainless steels in medical applications,» [Online]. Available: https://www.researchgate.net/publication/282819958_Use_of_stainless_steels_in_medical_applications.

## Indice delle figure

- FIG. 1 – IMMAGINE TRATTA DIRETTAMENTE DAL BREVETTO US 6,227,057B1 [1]	

- FIG. 2– SISTEMA DI RIFERIMENTO CONSIDERATO PER IL PIEDE DESTRO. LE TRE ROTAZIONI SONO STATE CLASSIFICATE RISPETTIVAMENTE COME YAW (Y) INTORNO L’ASSE Z, ROLL (R) INTORNO L’ASSE X E PITCH (P) INTORNO L’ASSE Y.	

- FIG. 3 - SONO RAFFIGURATI I NORMALI MOVIMENTI DI ROTAZIONE DELL’ARTICOLAZIONE DELLA CAVIGLIA. L’EVERSIONE E L’INVERSIONE INDICATO COME (R) OVVERO LA ROTAZIONE INTORNO L’ASSE X. LA FLESSIONE PLANTARE E DORSALE INDICATO COME (P) OVVERO LA ROTAZIONE INTORNO L’ASSE Y. L’ABDUZIONE E L’ADDUZIONE SPESSO INDICATE COME ROTAZIONE MEDIALE E LATERALE INDICATE COME (Y) OVVERO LA ROTAZIONE INTORNO L’ASSE Z.	

- FIG. 4 – RIABILITAZIONE FUNZIONALE PER LA CAVIGLIA	

- FIG. 5 – ASSI DI ROTAZIONE DELLE ARTICOLAZIONI TALOCRURALE E SUBTALARE [7]	

- FIG. 6 - MISURAZIONE IN SOLIDWORKS © DELLE ROTAZIONI NEL CASO DI FLESSIONE PLANTARE E DORSALE MEDIANTE LE RETTE PASSANTI PER I MARKER.	

- TAB. 1 – COPPIE (NM) CALCOLATE CON LA MEDIA DELLE FORZE MISURATE E IL BRACCIO MISURATO RISPETTO IL PUNTO DOVE È STATA ANCORATA LA FASCIA PER LE MISURE DELLE FORZE, TENENDO CONTO DELLA ROTAZIONE MEDIA.	

- FIG. 7 - DISTRIBUZIONE DELLE MISURE DELLE FORZE [NEWTON] EFFETTUATE NELLE 6 POSIZIONI LIMITE PER ENTRAMBI I PIEDI. LA CROCE EVIDENZIA LA MEDIA, VALORE CHE È STATO CONSIDERATO NEL RESTO DELLA TRATTAZIONE.	

- FIG. 8 – SONO RIPORTATI GLI STRUMENTI DI MISURA (A) OVVERO IL DINAMOMETRO, L’INCLINOMETRO, LE FASCETTE IN TESSUTO E UN CAVO INESTENSIBILE. IN (B) LA RAPPRESENTAZIONE GENERALE DI COME SONO STATE PRESE LE MISURE, PRECISAMENTE IL CASO DI FLESSIONE PLANTARE, CON LA FASCETTA IN TESSUTO NON ESTENSIBILE UTILIZZATA PER LE MISURE DELLA FORZA E IN (C)Z LA FASCETTA ELASTICA CON L’INCLINOMETRO. LE MISURE OTTENUTE CON L’INCLINOMETRO EFFETTUANDO TRE ROTAZIONI CONSECUTIVE IN ENTRAMBI I VERSI PRIMA PER INVERSIONE ED EVERSIONE (D), POI FLESSIONE PLANTARE E DORSALE (E) E INFINE PER LA ROTAZIONE MEDIALE E LATERALE (F). IN ROSSO SONO RAPPRESENTATI I VALORI MASSIMI (E MINIMI) OTTENUTI CALCOLANDO LA MEDIA TRA I MASSIMI (E MINIMI) OTTENUTI PER OGNUNA DELLE TRE ROTAZIONI NEI DUE PUNTI ESTREMALI.	

- TAB. 2 - ANGOLI DI MASSIMA ESCURSIONE MISURATI MEDIANTE SOLIDWORKS ©. SONO RIPORTATI I DATI SIA PER IL PIEDE DESTRO (DX) CHE SINISTRO (SX) PER LE TRE ROTAZIONI YAW (Y), ROLLO (R) E PITCH (P). I VALORI SONO RIPORTATI IN GRADI E APPROSSIMATI ALLA PRIMA CIFRA DECIMALE	

- TAB. 3 – MEDIA APPROSSIMATA DEI VALORI DI ROTAZIONE TRA PIEDE DESTRO E SINISTRO. GLI ANGOLI SONO CONSIDERATI IN MODULO, PER IL SEGNO FAR RIFERIMENTO AL MOVIMENTO E AL SISTEMA DI RIFERIMENTO.	

- FIG. 9 - LEGGE LINEARE PER LA MOLLA A GAS. FARE RIFERIMENTO ALLA RETTA DI COMPRESSIONE. DA CATALOGO VENGONO FORNITI I VALORI F1 ED FR, QUINDI È FACILMENTE CALCOLABILE IL VALORE F3 (MASSIMA ESTENSIONE), LA PENDENZA ED IL VALORE DI MASSIMA COMPRESSIONE.  STABILUS © – LIFT-O-MAT GAS SPRING	

- FIG. 10 – PRIMA BOZZA SCHEMATICA REALIZZATA A PARTIRE DAI DATI OTTENUTI TRAMITE IL CODICE MATLAB © CON IL FINE DI MANIPOLARE MEGLIO LE GEOMETRIE E AVERE DEI RIFERIMENTI PIÙ CONCRETI.	

- FIG. 11 - GEOMETRIA DI PARTENZA PER LA PEDANA	

- FIG. 12 – PEDANA COMPLETA CON LA COPERTURA SUPERFICIALE IN MATERIALE POLIMERICO. PRESENTE ANCHE IL SISTEMA DI RIFERIMENTO SOLIDALE ALLA PEDANA E IL CENTRO DI MASSA.	

- FIG. 13 – VISTA INFERIORE DELLA PEDANA. SI VEDONO I TACCHETTI PER I FORI, LA SEDE PER IL GIUNTO SFERICO E LA FORMA GENERALE VALUTATA COME IPOTESI PER ELIMINARE DEL MATERIALE QUALORA FOSSE RISULTATO NECESSARIO.	

- FIG. 14 - PRIMO PROTOTIPO “WISHBONE” PER IL BRACCIO DI SUPPORTO	

- FIG. 15 - I MODELLI DI BRACCIO DI SUPPORTO “GEOMETRIA AD Y”. SOPRA UNA BOZZA E SOTTO IL MODELLO DEFINITIVO.	

- FIG. 16 – FOTO DEI PRIMI PROTOTIPI PER LA BASE	

- FIG. 17 – MODELLO DELLA BASE CON FORMA AD H	

- FIG. 18 – IMMAGINE DEL CAPPUCCIO TERMINATA LA PRIMA MODELLAZIONE	

- FIG. 19 – INTERSEZIONE TRA LA COPERTURA SFERICA E IL PERNO DI ACCOPPIAMENTO NELLA POSIZIONE DI RIPOSO (PEDANA A 30° RISPETTO L’ORIZZONTALE).	

- FIG. 20 - VISTA PARALLELA ALLA PIASTRINA DI ACCOPPIAMENTO DELLO SCHIZZO 3D DELLE VARIE CURVE DI INTERSEZIONE	

- FIG. 21 – VISTA PERPENDICOLARE PARALLELA ALLA PIASTRINA DI ACCOPPIAMENTO.	

- FIG. 22 – ASSIEME BOZZA UTILIZZATO PER FARE DIVERSE MISURE E VERIFICHE	

- FIG. 23 – PISTONE CENTRALE MODIFICATO CON LE MISURE OFFERTE DAL CATALOGO STABILUS ©	

- FIG. 24 – PISTONE LATERALE MODIFICATO CON LE MISURE OFFERTE DAL CATALOGO STABILUS ©.	

- FIG. 25 – PERNI CON TESTA SFERICA. A SINISTRA QUELLO TRA PISTONI LATERALI E BASE E A DESTRA QUELLO TRA I PISTONI E I RESTANTI PUNTI DI COLLEGAMENTO.	

- FIG. 26 – COMPENETRAZIONE NEL GIUNTO SFERICO A SEGUITO DI UNA FLESSIONE DORSALE DI 42° (VALORE MASSIMO)	

- FIG. 27 – SOMMA DI F1 ED FR SUL PISTONE CENTRALE IN FASE DI SIMULAZIONE	

- FIG. 28 – MOLLA ELASTICA SUL PISTONE CENTRALE IN FASE DI SIMULAZIONE	

- FIG. 29 – ANGOLO DI PITCH PER LA FLESSIONE PLANTARE	

- FIG. 30 – IN FIGURA È RIPORTATO L’ASSIEME PRINCIPALE UTILIZZATO PER LE SIMULAZIONI. NELLA COLONNA CENTRALE LE POSIZIONI DI RIPOSO E NELLE COLONNE LATERALI LE POSIZIONI AI LIMITI ARTICOLARI.	

- FIG. 31 – ANGOLO DI PITCH PER LA FLESSIONE DORSALE	

- FIG. 32 – ANGOLO DI YAW PER LA ROTAZIONE	

- FIG. 33 – ANGOLO DI ROLL PER L’EVERSIONE	

- FIG. 34 – ANGOLI DI ROTAZIONE PER PITCH + ROLL	

- FIG. 35 – COPPIA DEL MOTORE NECESSARIA AD IMPORRE UNO SPOSTAMENTO DI FLESSIONE PLANTARE PARI A QUELLO MISURATO SPERIMENTALMENTE	

- FIG. 36 - COPPIA DEL MOTORE NECESSARIA AD IMPORRE UNO SPOSTAMENTO DI FLESSIONE DORSALE PARI A QUELLO MISURATO SPERIMENTALMENTE	

- FIG. 37 - COPPIA DEL MOTORE NECESSARIA AD IMPORRE UNO SPOSTAMENTO DI YAW PARI A QUELLO MISURATO SPERIMENTALMENTE	

- FIG. 38 - COPPIA DEL MOTORE NECESSARIA AD IMPORRE UNO SPOSTAMENTO DI ROLL PARI A QUELLO MISURATO SPERIMENTALMENTE	

- FIG. 39 – COPPIA SIMULATA DEL MOTORE PER LA CLASSE 1	

- FIG. 40 – SPOSTAMENTO IMPOSTO DAL MOTORE PER LA CLASSE 1	

- FIG. 41 - COPPIA SIMULATA DEL MOTORE PER LA CLASSE 2	

- FIG. 42 - SPOSTAMENTO IMPOSTO DAL MOTORE PER LA CLASSE 2	

- FIG. 43 – VISTA IN SEZIONE DEL MODELLO FINALE DELLA BASE	

- FIG. 44 – VISTA IN TRASPARENZA DEL SISTEMA DI ANCORAGGIO PER I PISTONI LATERALI CON UN CUSCINETTO A SFERA	

- FIG. 45 - VISTA IN SEZIONE DEL SISTEMA DI ANCORAGGIO PER I PISTONI LATERALI CON UN CUSCINETTO A SFERA	

- FIG. 46 - VISTA LATERALE	

- FIG. 47 – VISTA FRONTALE	

- FIG. 48 – VISTA SUPERIORE	

- FIG. 49 – VISTA INFERIORE	

- FIG. 50 – PARTICOLARE SULL’ESTREMITÀ DELLA BASE	

- FIG. 51 – INGRANDIMENTO SUL GIUNTO	

## Figure extra 

 

> **Fig. 46** - Vista laterale

 

> **Fig. 47** – Vista frontale

 

> **Fig. 48** – Vista superiore

 

> **Fig. 49** – Vista inferiore

 

> **Fig. 50** – Particolare sull’estremità della base 

 

> **Fig. 51** – Ingrandimento sul giunto

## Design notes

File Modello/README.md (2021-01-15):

# Modello CAD completo
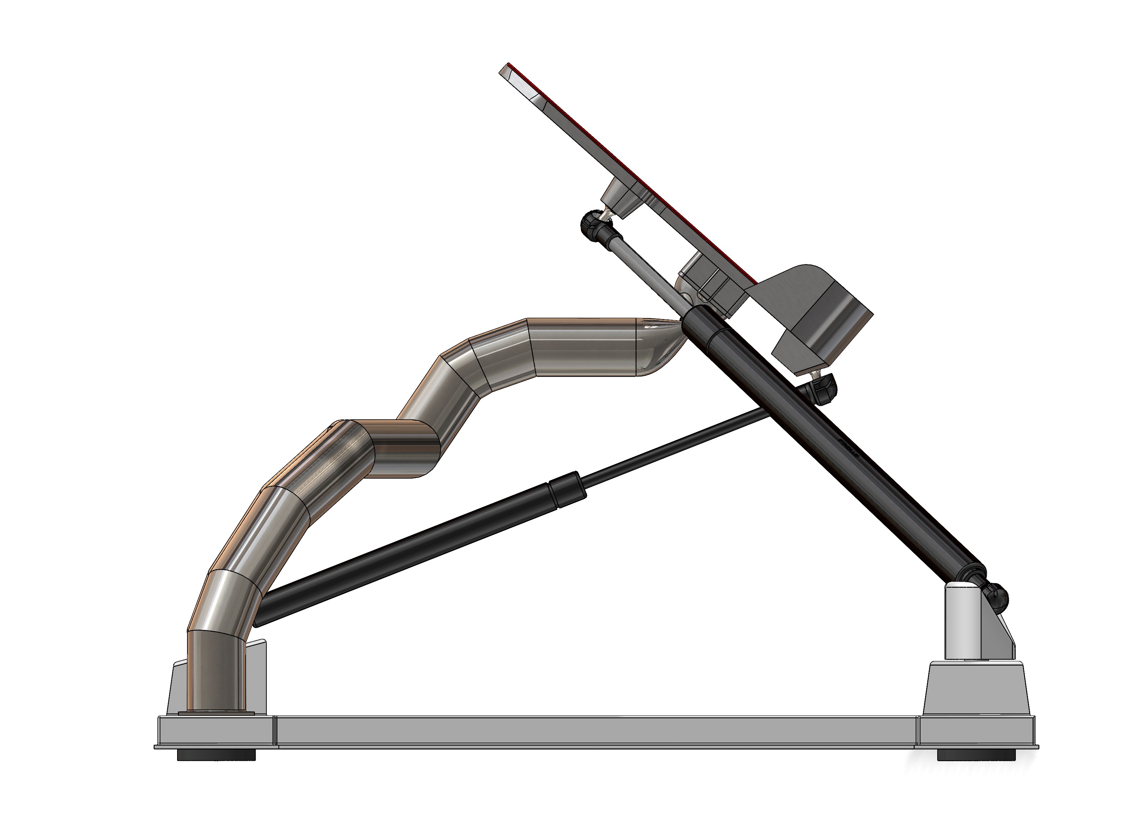
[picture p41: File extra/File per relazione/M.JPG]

> Fig. 46 - Vista laterale

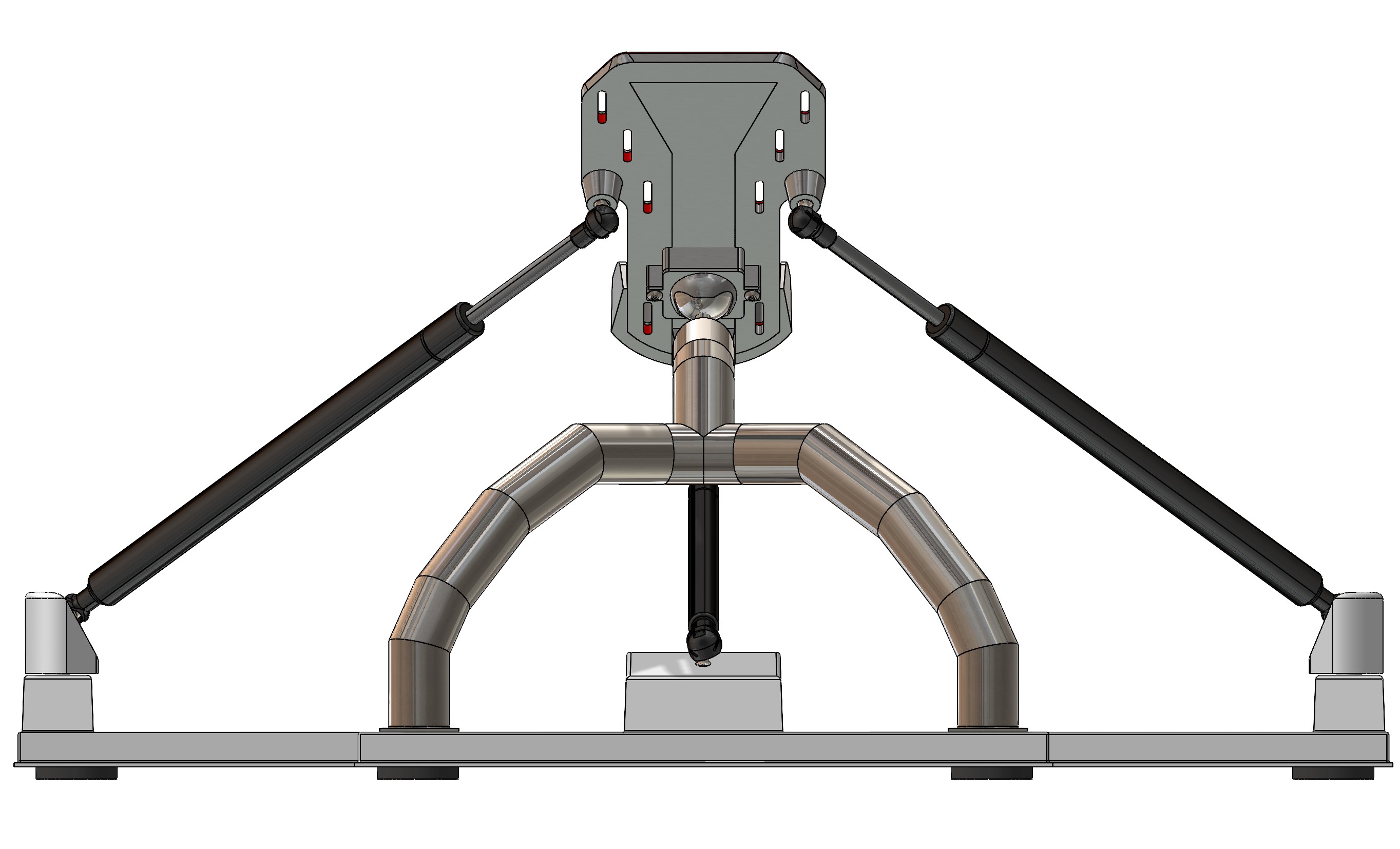
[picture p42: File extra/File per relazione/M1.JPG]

> Fig. 47 – Vista frontale

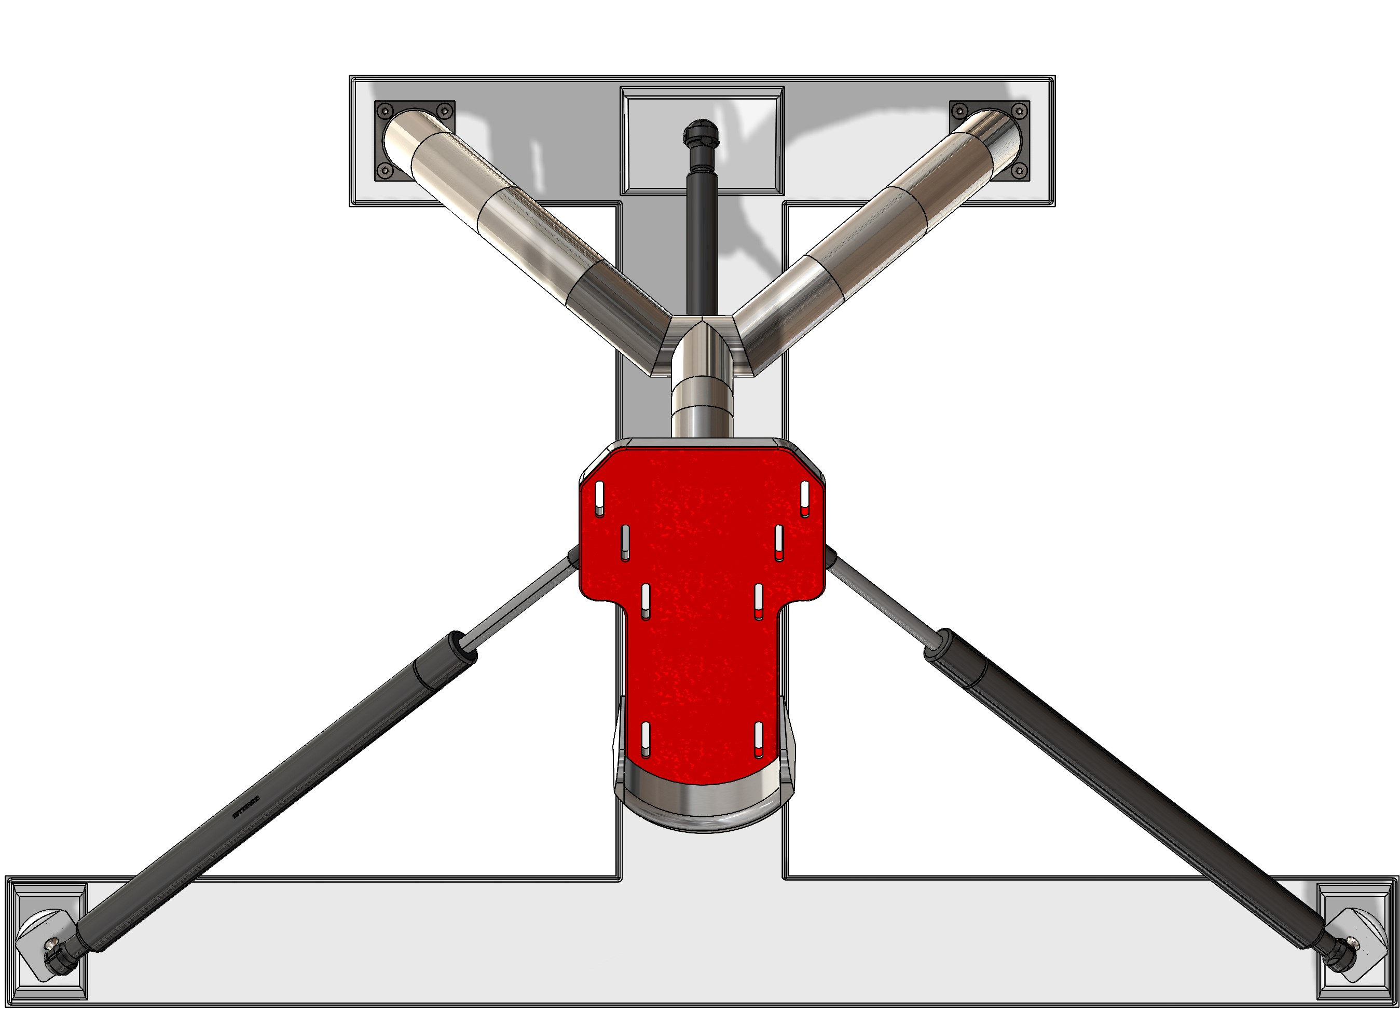
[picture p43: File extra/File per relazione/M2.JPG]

> Fig. 48 – Vista superiore

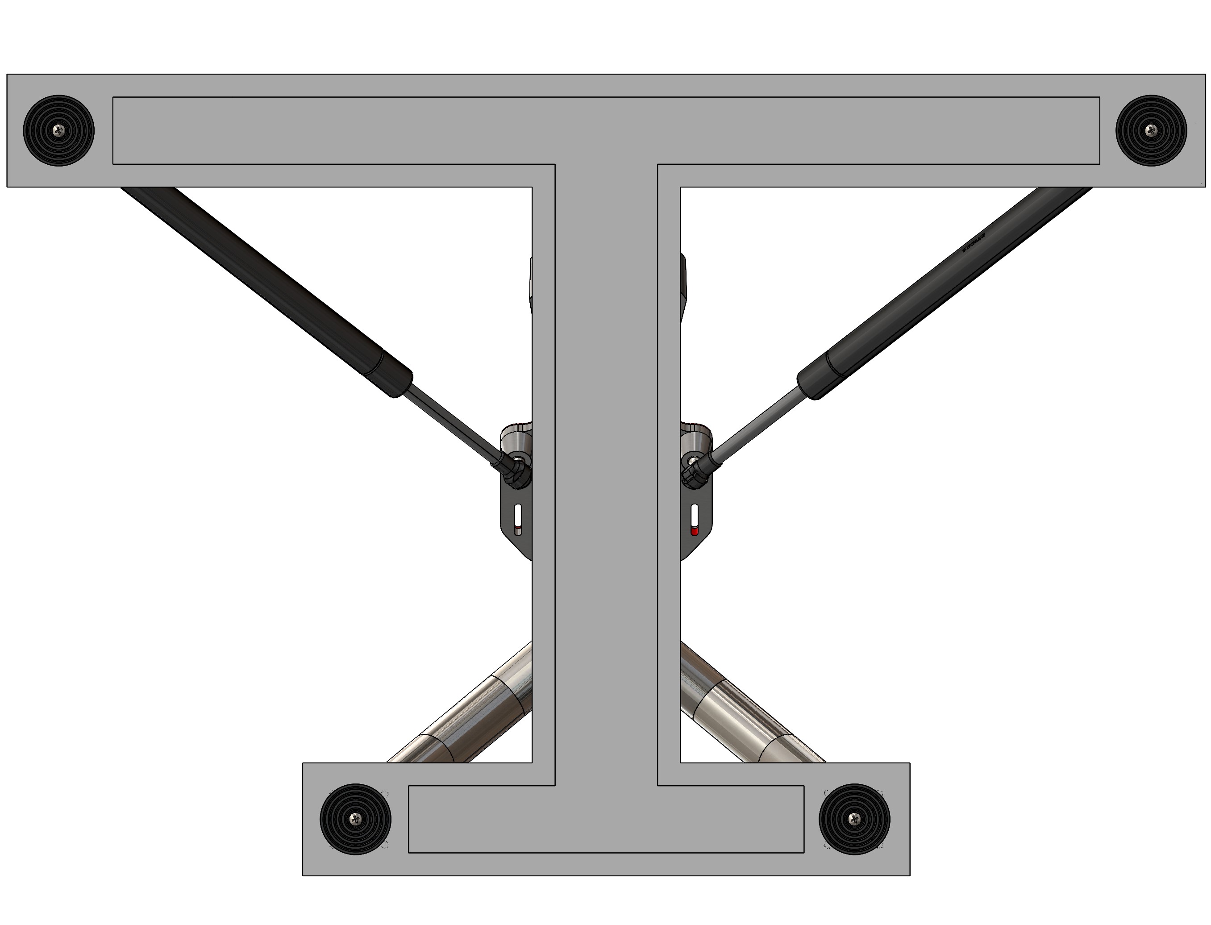
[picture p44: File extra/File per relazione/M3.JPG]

> Fig. 49 – Vista inferiore

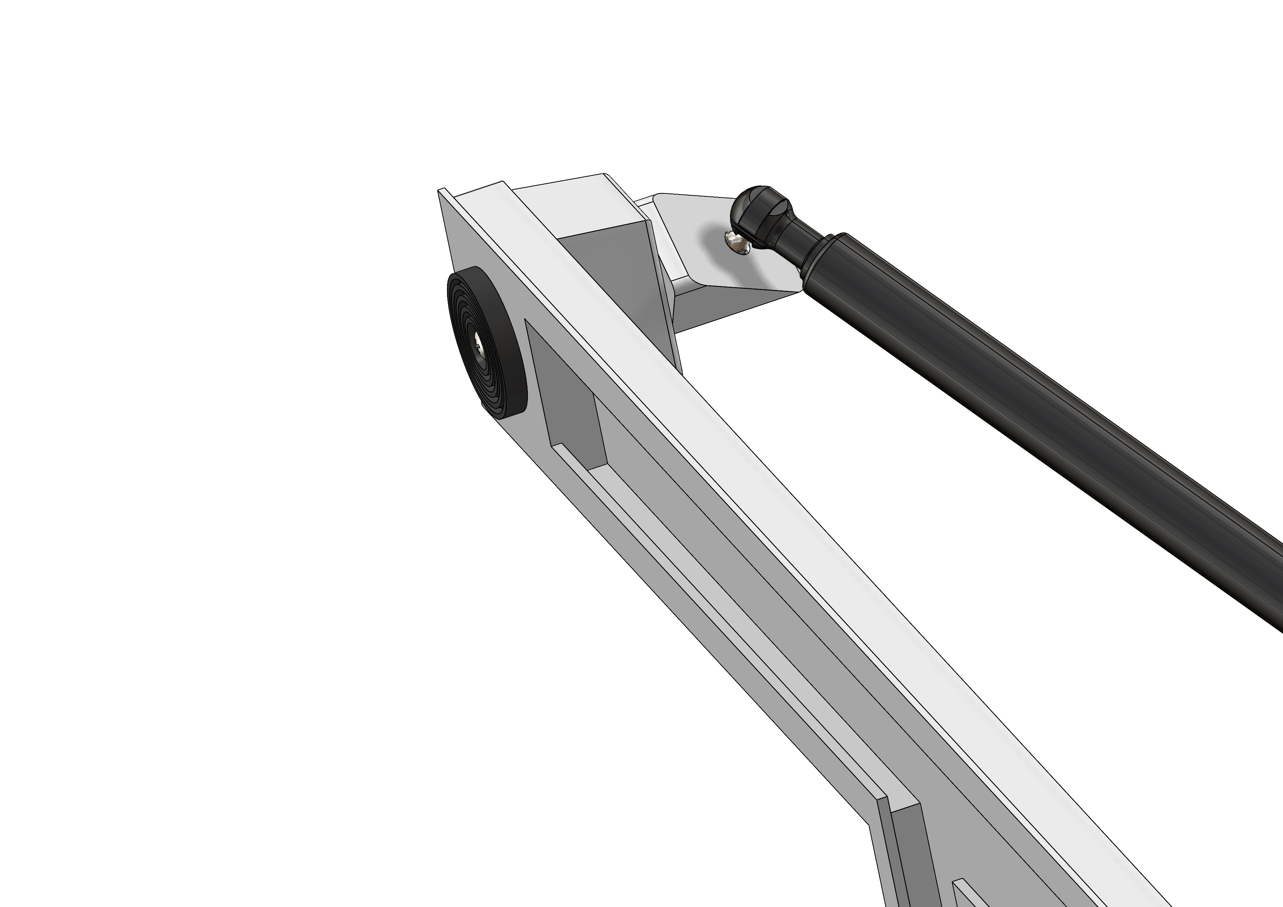
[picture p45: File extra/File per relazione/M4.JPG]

> Fig. 50 – Particolare sull’estremità della base

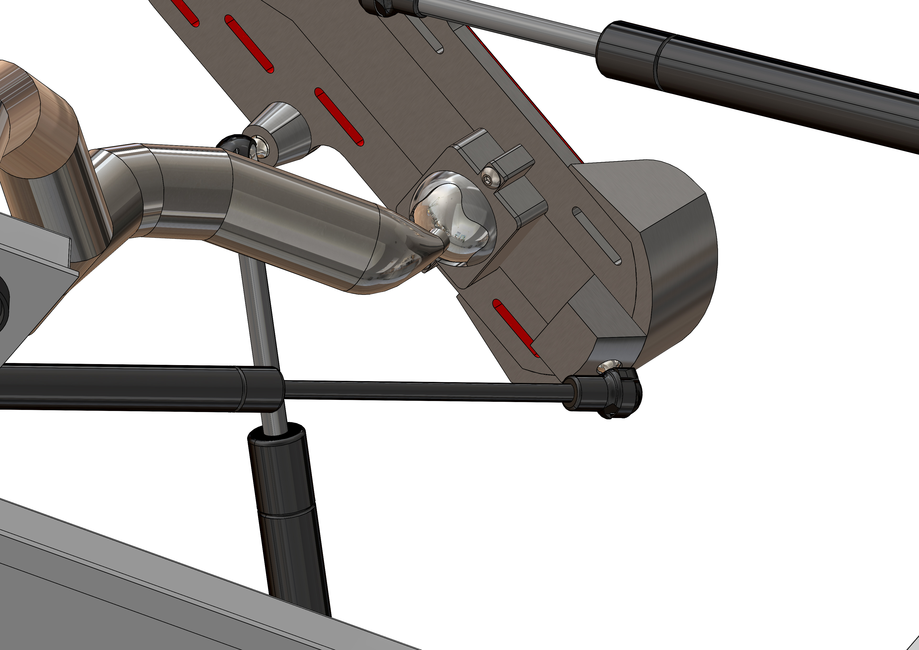
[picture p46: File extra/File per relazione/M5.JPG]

> Fig. 51 – Ingrandimento sul giunto

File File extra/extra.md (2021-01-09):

# Extra 

All'interno di questa cartella si trovano i file complementari al progetto e tutto quello che non è stato possibile inserire all'interno della relazione.
------------
Albero cartelle

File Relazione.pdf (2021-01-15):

# Progetto Bioprotesi a.a. 2020/2021

# Ad opera di

# Blasi Luca e Mastrofini Alessandro

## Indice

## Introduzione

La seguente relazione ha come obiettivo di spiegare accuratamente quali sono stati i passaggi logici che hanno portato alla creazione del prototipo di un sistema riabilitativo per la caviglia. Il brevetto fornitoci è stata fonte di ispirazione per il numero di componenti e come queste si relazionassero tra di loro. Per la forma di queste abbiamo deciso di deviare dal design originale, optando per piccole variazioni di natura principalmente stilistica. I dettagli e i motivi di queste modifiche saranno presentati più avanti.
In questa relazione è presente anche un attento studio ai materiali e come questi possano inficiare il funzionamento del progetto o come possano invece portare grandi vantaggi.
Il brevetto US 6,277,057B1 [1] fornisce una attenta descrizione del dispositivo che riassumeremo brevemente al fine di facilitare la lettura e comprensione della relazione.
Il dispositivo si compone principalmente delle seguenti parti:
- base
- braccio di supporto
- pedana
- apparati resistivi
La base è la componente che fornisce stabilità al dispositivo e durante l’utilizzo sarà poggiata a terra. Collegato alla base abbiamo il braccio di supporto che si estende ortogonalmente per il primo tratto dalla base per poi portarsi verso il centro di questa, ad una determinata quota dalla base. All’estremità di questo troveremo una estensione che la collega a una sfera. Quest’ultimo elemento sarà essenziale per la composizione del “ball and socket joint” che permetterà alla pedana di ruotare per creare i movimenti cardine della riabilitazione. Sulla suddetta pedana il paziente potrà poggiare il piede la cui caviglia necessita esercizio. Al di sotto di questa pedana

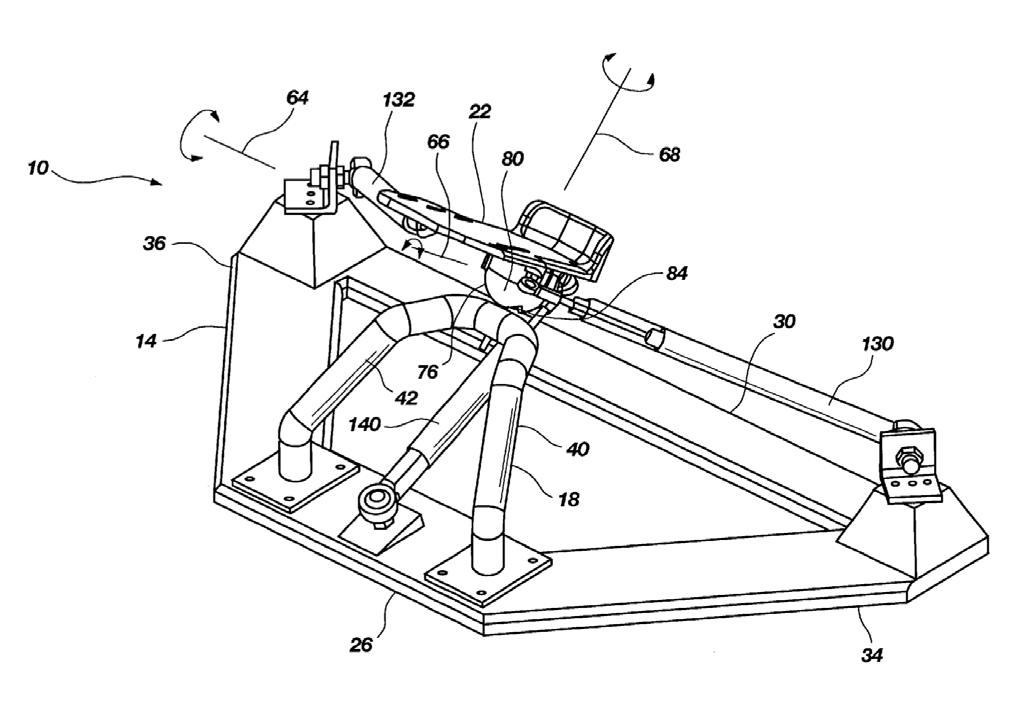
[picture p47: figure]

troviamo il socket, una cavità che permette di accogliere la sfera citata prima. Questa cavità coprirà la sfera in modo tale da bloccare le traslazioni relative tra braccio di supporto e pedana. Sarà modellata in modo tale da permettere la rotazione della sfera entro certi limiti, aspetto che discuteremo successivamente.
Questo giunto appena descritto quindi collega il braccio di supporto e la pedana, permettendone le rotazioni relative. Considerato come il braccio di supporto sia ancorato alla base sarà quindi possibile immaginare la pedana sollevata da terra e libera di ruotare.
Alla stessa pedana sono anche collegati quelli che il brevetto definisce come “resistive means”, ossia congegni capaci di opporre resistenza ad allungamento ed accorciamento. Questi congegni collegheranno direttamente la pedana alla base, con l’obiettivo di opporre resistenza, elemento fondamentale della riabilitazione. Facendo riferimento alle normative ISO 20957-1 per le attrezzature da allenamento e la normativa ISO 14971 per la gestione del rischio per i dispostivi medicali abbiamo cercato di focalizzaci su un dispositivo semplice e con bassi costi di produzione e manutenzione che garantisse un certo comfort all’utilizzatore ma che al contempo fosse stabile durante il movimento e riducesse al minimo la possibilità di ulteriori infortuni. Essendo un dispositivo di

Fig. 1 – Immagine tratta direttamente dal brevetto US 6,227,057B1 [1]

riabilitazione deve garantire il corretto movimento articolare in tutte le direzioni e permettere un certo lavoro tale da favorire la rigenerazione corretta dei tessuti danneggiati ma allo stesso tempo deve limitare movimenti troppo bruschi e bloccare il movimento ai limiti articolari prevenendo ulteriori infortuni [2, 3, 4, 5].
Il dispositivo, per come è stato strutturato, prevede sia un carico isometrico ai limiti articolari sia un intenso esercizio propriocettivo volto ad ottimizzare il recupero della cinematica articolare.
Una particolare attenzione è stata dedicata anche alla scelta di un materiale che risultasse quanto più possibile anallergico e resistente alla corrosione data da un eventuale pulizia e sanificazione intensiva nel caso venisse utilizzato da più utenti, come all’interno di uno studio medico.

## Misure e valutazioni iniziali

Una prima valutazione è stata fatta cercando in letteratura un modello semplice ma sufficientemente accurato che descrivesse la cinematica della caviglia in un modo che risultasse utile allo sviluppo del progetto.

Fig. 2– Sistema di riferimento considerato per il piede destro. Le tre rotazioni sono state classificate rispettivamente come yaw (Y) intorno l’asse z, roll (R) intorno l’asse x e pitch (P) intorno l’asse y.

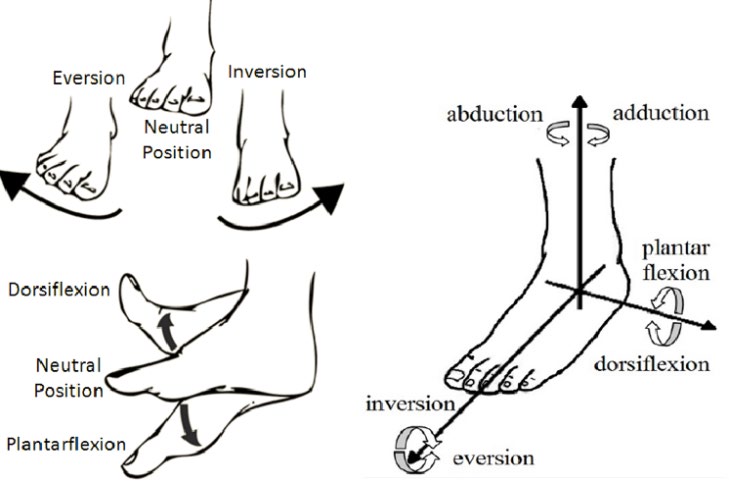
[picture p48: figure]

Fig. 3 - Sono raffigurati i normali movimenti di rotazione dell’articolazione della caviglia. L’eversione e l’inversione indicato come (R) ovvero la rotazione intorno l’asse x. La flessione plantare e dorsale indicato come (P) ovvero la rotazione intorno l’asse y. L’abduzione e l’adduzione spesso indicate come rotazione mediale e laterale indicate come (Y) ovvero la rotazione intorno l’asse z.
Cinematica della caviglia
La caviglia unisce il segmento della gamba con il piede. È formata dall’unione di tre ossa: tibia, fibula e talo e da numerosi legamenti che le tengono unite e le stabilizzano. Come le altre articolazioni della gamba è responsabile del supporto del peso dell’intero corpo e richiede un’ottima rigidezza tendinea e muscolare.
Ci sono 28 ossa e 26 articolazioni in ogni piede e caviglia che permettono un insieme di diversi movimenti e l’assorbimento della forza peso nel caso stazionario e di forze molto più intense nel caso di corsa o di impatti violenti come nei salti. Gran parte delle articolazioni sono delle anfiartrosi con legamenti molto rigidi che permettono soltanto movimenti minimi tuttavia conferiscono al piede una notevole flessibilità elastica e consentono di distribuire i carichi di compressione agenti in tensioni elastiche sui legamenti di una struttura complessivamente leggera. L’escursione del piede è variabile da persona a persona e con l’età ed è bene sottolineare il fatto che l’escursione complessiva data sia dall’articolazione talocrurale che subtalare è notevolmente maggiore della somma delle escursioni di ogni singola articolazione la ragione di tale fenomeno risiede nei legamenti il cui grado di tensione può essere

aumentato o ridotto a seconda dei movimenti delle strutture adiacenti. L’articolazione talocrurale è formata dalla tibia, dalla fibula (o perone) e dalla troclea dell’astragalo e dai numerosi legamenti e capsula articolare necessari alla stabilizzazione. È un’articolazione a cerniera il cui asse decorre trasversalmente attraverso la forchetta malleolare e la troclea dell’astragalo.
L’articolazione subtalare è costituita da due articolazioni anatomicamente distinte ma che funzionano all’unisono permettendo una rotazione mediante un asse che decorre obliquamente attraverso il tarso. Si può distinguere un’articolazione anteriore con l’osso navicolare ed in una posteriore con il calcagno. Fig. 5
Le due articolazioni sono strettamente collegate tra loro dal punto di vista funzionale e l’una permette di ampliare lo spazio di movimento dell’altra [6].

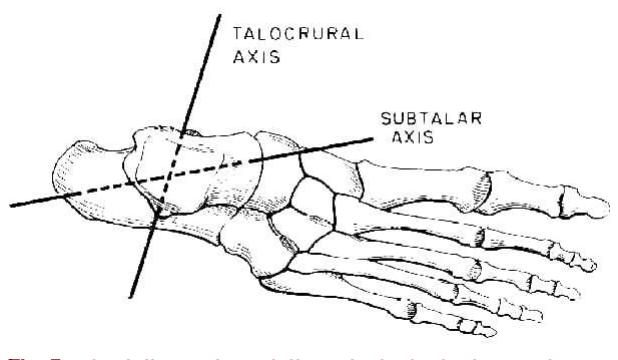
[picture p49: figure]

Fig. 5 – Assi di rotazione delle articolazioni talocrurale e subtalare [7]

Le lesioni più comuni sono le distorsioni e al secondo posto le fratture. Mentre la frattura prevede l’interruzione della continuità ossea, la distorsione indica tutte le lesioni delle articolazioni e dei tessuti molli ad esse legati, provocati da movimenti anomali che eccedono i limiti fisiologici delle articolazioni. Il trattamento per queste lesioni prevede le seguenti fasi:
- Trattamento per eventuali emorragie, ghiaccio, bendaggi compressivi, antiinfiammatori
- Inizio del recupero con una fase attiva volta a ripristinare la mobilità articolare. Inizia da 1 a 3 settimane dopo la lesione
- Inizio di movimenti complessi compresa l’attività sportiva mantenendo comunque gli esercizi di recupero.
Gli esercizi di riabilitazione per la caviglia prevedendo un basso carico, una lunga durata e una forte ripetitività dei movimenti. [8]
È importante notare come oltre a migliorare la forza e la resistenza dell’articolazione i pazienti devono anche accrescere la propriocezione garantendo una maggiore stabilità alla caviglia. Una mancanza di propriocezione porta ad una maggior debolezza articolare e quindi ad un elevato rischio di lesione pertanto è necessario prevedere una riabilitazione che considera anche questi fattori [9, 10].
In letteratura si trovano sostanzialmente tre categorie di modelli cinematici: articolazione talocrurale e subtalare rappresentati come un giunto cilindrico, la caviglia che viene

Fig. 4 – Riabilitazione funzionale per la caviglia rappresentata come un giunto sferico oppure la caviglia viene rappresentata come un quadrilatero articolato [11].
Una descrizione sufficientemente accurata per il progetto in questione è stata identificata nella pubblicazione di C. Brockett [12]. Consideriamo quindi tre diversi assi di rotazione (Fig. 2) sui quali possiamo identificare una rotazione positiva ed una negativa rispetto al piano neutro. Questo ci porta ad identificare 6 rotazioni indicate in Fig. 3, tratta dalla pubblicazione di C. Racu [13].
È anche opportuno considerare il rapporto tra la forza 1 RM, ovvero il carico che consente una sola ripetizione di un movimento, nonché il carico massimale, e il numero di ripetizioni tipicamente possibili per una certa frazione di questo carico. Come mostrato in letteratura tipicamente lavorando al 60% del carico è possibile effettuare più di 20 ripetizioni [14, 15]. Inoltre, è necessario considerare che trattandosi di riabilitazione è bene rimanere distanti dal carico massimo e lavorare ad una percentuale del carico massimo molto bassa riuscendo così ad effettuare un elevato numero di ripetizioni provocando una quantità di stress sufficiente ad indurre una risposta dai tessuti danneggiati ma ben lontana sia dalla soglia di dolore che dal punto in cui potrebbero provocarsi altri danni ad un tessuto che non ha ancora recuperato del tutto le sue funzionalità.
Parlando di carico massimo in questo caso facciamo riferimento alle forze misurate ai limiti articolari in una posizione isometrica che quindi sappiamo essere tra le forze più elevate a cui può essere sottoposta l’articolazione [16], di cui parleremo più avanti.
Mentre in una fase tardiva della riabilitazione può essere utile aumentare il carico nell’ottica di indurre un rafforzamento dell’intera articolazione.
Un altro fattore interessante è quello che avendo il dispositivo dei blocchi ai limiti articolari è anche possibile, dopo aver portato il piede al limite articolare desiderato, effettuare delle sessioni di isometria, anch’esse molto utili dal punto di vista riabilitativo.
Questi esercizi sono comunque pensati nel rispetto di diverse linee guida ormai note in letteratura [17] ed è consigliato comunque un consulto con un fisioterapista al fine di programmare e ottimizzare le singole procedure in dettaglio.
Si è quindi reso necessario ottenere delle misure che ci permettessero di dimensionare correttamente sia i limiti articolari del dispositivo che la giusta resistenza esercitata dai pistoni
Prima di procedere alle misure ci è sembrato necessario scegliere un sistema di riferimento per rendere più chiaro e coerente tutto il progetto. Il sistema di riferimento è stato preso come una terna destra con l’asse z orientato lungo la tibia, un asse x orientato lungo le dita del piede e un asse y perpendicolare ad entrambi. (Fig. 2) La trattazione è stata eseguita rappresentando principalmente il piede destro, tuttavia, il dispositivo può funzionare con entrambi i piedi ed è stato dimensionando considerando dei valori medi tra i due piedi e cercando di mantenere il più possibile la simmetria.

Fig. 6 - Misurazione in SOLIDWORKS © delle rotazioni nel caso di flessione plantare e dorsale mediante le rette passanti per i marker.

Misure strumentali
Le misure sono state effettuate per entrambi i piedi.
Le prime misure rilevate sono state le dimensioni della pianta del piede destro e sinistro 25cmx9cm e successivamente sono state acquisite le immagini delle rotazioni sui tre assi considerati. Le immagini sono state acquisite con una ripresa a 60 frame al secondo da cui sono stati successivamente estratti i frame corrispondenti ai punti estremali delle rotazioni. Per rendere più precise le successive elaborazioni sono stati segnati sul piede alcuni marker con un pennarello (spiegato nel paragrafo seguente) e la ripresa è stata effettuata ponendo la camera quanto più possibile parallela al piano dove avveniva la rotazione e quanto più orizzontale possibile.
Successivamente sono state misurate le forze espresse nei punti estremali delle rotazioni per i movimenti di flessione plantare e dorsale, rotazione mediale e laterale, eversione e inversione.
Il valore è stato misurato nella direzione parallela agli assi di riferimento.
Sono stati raccolti tre valori per ogni situazione e ne è stata presa la media tra il piede destro e il piede sinistro.
I valori sono stati raccolti mediante l’uso di un dinamometro digitale con una precisione di 10g [18] che forniva una misura di massa, quindi convertiti in forza peso.
Il dinamometro è stato collegato al piede mediante una fascia in tessuto non elastico, un gancio e un cavo rigido Fig. 8
I valori sono raccolti in Fig. 7 e Tab. 1. Coppia
Flessione plantare | 6,6
Flessione dorsale | 10,0
Eversione | 1,5
Inversione | 1,7
Rotazione laterale | 13,1
Rotazione mediale | 10,9
Tab. 1 – Coppie (Nm) calcolate con la media delle forze misurate e il braccio misurato rispetto il punto dove è stata ancorata la fascia per le misure delle forze, tenendo conto della rotazione media.

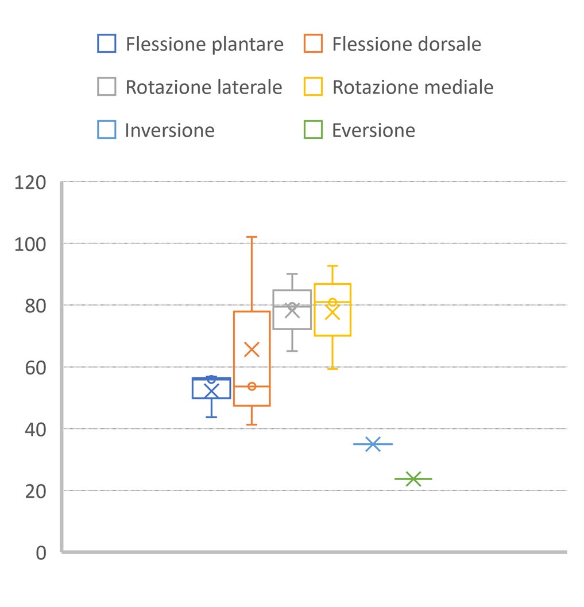
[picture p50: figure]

Fig. 7 - Distribuzione delle misure delle forze [Newton] effettuate nelle 6 posizioni limite per entrambi i piedi. La croce evidenzia la media, valore che è stato considerato nel resto della trattazione.
Le varie misure sono state effettuate in diverse giornate e in momenti diversi della giornata al fine di stimare una media che non fosse alterata dallo stato di fatica dell’articolazione.
Per avere un’ulteriore conferma sono state effettuate delle misure anche con un inclinometro [19] al fine di avere un secondo riscontro sulle misure angolari Fig. 8. Il dispositivo è stato ancorato al piede mediante una fascia elastica che lo ha mantenuto stabile e solidale al piede. Durante i movimenti si è cercato di mantenere la pianta del piede quanto più dritta possibile cercando di evitare possibili artefatti dovuti alla curvatura del piede. Valutazioni al calcolatore
Successivamente sono stati elaborati i video estraendone i frame negli istanti di massima rotazione. Sui singoli frame sono stati applicati diversi filtri per rendere più
marcato il contrasto sia tra il piede e lo sfondo sia tra piede e marker. I file immagine sono stati importati all’interno del software SOLIDWORKS © nell’ambiente di schizzo.

Prima è stata importata l’immagine nella posizione neutra tracciando un segmento tra i marker e scalando l’immagine in modo tale che il piede risultasse esattamente in scala 1:1 sulla base delle misure precedentemente effettuate.
Poi sono state importate le immagini delle due rotazioni estremali e impostate in trasparenza in modo tale da vedere la posizione neutra. Nuovamente sono stati uniti i marker con un segmento. Mediante lo strumento “misura intelligente” sono state valutate le rispettive inclinazioni nei due punti estremali delle rotazioni Fig. 6.
Lo stesso procedimento è stato effettuato per tutti e tre gli assi.
I dati risultanti sono raccolti in Tab. 2. Quindi è stata presa la media tra piede destro e sinistro Tab. 3.
Le approssimazioni e le imprecisioni le assumiamo trascurabili poiché stiamo affrontando un organismo biologico, per altro in una fase riabilitativa, quindi l’effettivo stato e i movimenti potrebbero cambiare di seduta in seduta e dipendere dallo stato psicologico, stress prodotto dalle sedute precedenti, risposte infiammatorie dei tessuti e tanti altri fattori che rendono accettabile un certo grado di incertezza.
Y | | R | | P
DX | SX | DX | SX | DX | SX
+28,1 | +39,82 | +11,5 | +27,52 | +28,3 | +19,17
-48,1 | -42,91 | -51,3 | -39,33 | -43,7 | -39,71
Tab. 2 - Angoli di massima escursione misurati mediante SOLIDWORKS ©. Sono riportati i dati sia per il piede destro (DX) che sinistro (SX) per le tre rotazioni yaw (Y), roll (R) e pitch (P). I valori sono riportati in gradi e approssimati alla prima cifra decimale
| | | Gradi
Flessione plantare | 24°
Flessione dorsale | 42°
Eversione | 39°
Inversione | 20°
Rotazione laterale | 46°
Rotazione mediale | 34°
Tab. 3 – Media approssimata dei valori di rotazione tra piede destro e sinistro. Gli angoli sono considerati in modulo, per il segno far riferimento al movimento e al sistema di riferimento.

Fig. 8 – Sono riportati gli strumenti di misura (a) ovvero il dinamometro, l’inclinometro, le fascette in tessuto e un cavo inestensibile. In (b) la rappresentazione generale di come sono state prese le misure, precisamente il caso di flessione plantare, con la fascetta in tessuto non estensibile utilizzata per le misure della forza e in (c) la fascetta elastica con l’inclinometro. Le misure ottenute con l’inclinometro effettuando tre rotazioni consecutive in entrambi i versi prima per inversione ed eversione (d), poi flessione plantare e dorsale (e) e infine per la rotazione mediale e laterale (f). In rosso sono rappresentati i valori massimi (e minimi) ottenuti calcolando la media tra i massimi (e minimi) ottenuti per ognuna delle tre rotazioni nei due punti estremali.

I dati ottenuti sono stati anche controllati con diversi studi in letteratura (ROM, Pitch: 65 ÷75°, Yaw:35 ° [12]; Pitch:65÷70°, Roll:25°, Yaw:25÷30° [20]; Pitch:60°, Yaw:60° [21]; Pitch:50÷70°, Roll:50° [22]) trovando diverse corrispondenze e con le varie differenze che rientrano nella naturale variabilità biologica. Discorso analogo per le forze/coppie misurate.

## Progetto

Considerazioni iniziali
Per dimensionare la pedana si è tenuto conto di diversi aspetti.
È stato implementato un codice MATLAB © che ci permettesse di considerare la curva di carico dei pistoni e loro inclinazione per calcolare la risultante a rotazione intorno agli assi solidali alla pedana in modo da minimizzarla.
Essendo il problema con infinite soluzioni e troppe incognite per un calcolo puramente numerico sono stati considerati altri fattori come la comodità dell’utilizzatore e una dimensione complessiva tale da rendere l’oggetto abbastanza contenuto e trasportabile ma allo stesso tempo sufficientemente stabile e robusto. Queste considerazioni ci hanno fatto optare per una posizione di riposo con un’inclinazione della pedana di circa 30° e l’idea di rimanere con delle dimensioni della base non superiori ai 70cm x 50cm. Le stesse considerazioni ci hanno fatto optare per una disposizione dei pistoni laterali simmetrica e una disposizione del pistone centrale sul piano xz.
Queste considerazioni geometriche ci hanno aiutato a vincolare le escursioni dei pistoni e quindi la loro inclinazione (ulteriori considerazioni sono state fatte nei paragrafi seguenti).
Scelta dei pistoni
Per la scelta dei pistoni abbiamo consultato il catalogo dell’azienda Stabilus © optando per la serie di molle a gas “LIFT-O-MAT” nella serie “Inox Line” in acciaio inossidabile [23].
È stata valutata l’espressione della forza in compressione/estensione riformulando quanto dichiarato dall’azienda come la legge elastica:

# FF(ll) = FFRR + FF1 + FF1(xx−1)

llmmmmmm

ll (1)

Questa formula è stata ottenuta considerando i valori forniti da catalogo

# (FF1, FFRR, llmmmm , xx = FF1

FF2
) e considerando il caso
peggiore per le valutazioni necessarie al progetto ovvero il caso di forza massima in compressione quindi considerando anche la

componente FFRR.

Essendo una legge lineare è intuitiva la rappresentazione

# FF(ll) = FF1 + FFRR + mm

dove:

# mm = FF2 − FF1

llmmmm

# = FF1(xx − 1)

llmmmm

e allora si ottiene la relazione (1).
Per i valori indicati si piò fare riferimento alla Fig. 9.
Per la scelta dei pistoni “Inox Line” siamo rimasti fedeli ai valori di catalogo con FR=60N, x=1,35 e per F1 un valore di partenza di 100N con incrementi di 25N. I valori di F1 vincolano anche la lunghezza di massima estensione e quindi la lunghezza massima del pistone tra i due attacchi.
Il codice MATLAB © ci ha aiutato a calcolare una disposizione dei pistoni sulla piattaforma tale da garantire un momento risultante intorno gli assi quanto più basso possibile. Qui abbiamo dovuto procedere per tentativi cercando di rispettare le considerazioni iniziali e arrivando a trovare una prima stima con i fori per i pistoni laterali ad una distanza di 65cm dalle y e una distanza di 5cm dall’asse x. Per il pistone posteriore invece una distanza di 50cm dall’asse y.
Questi valori si riferiscono ad un sistema di riferimento come indicato in Fig. 2 e con origine il centro della rotazione.

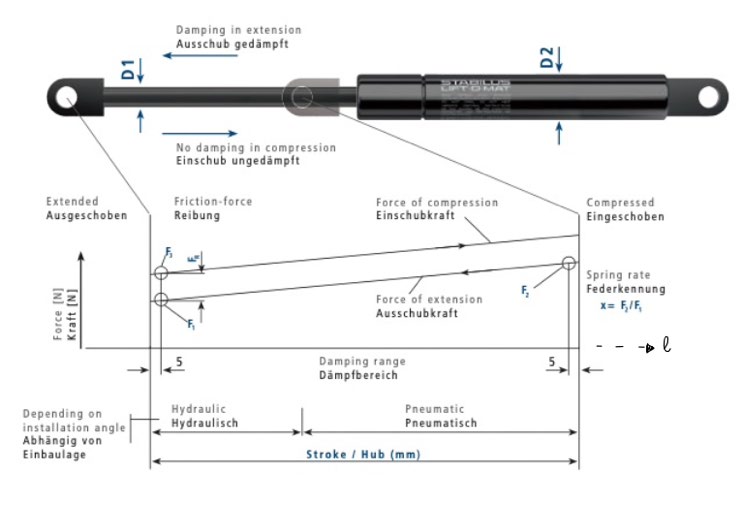
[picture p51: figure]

Fig. 9 - Legge lineare per la molla a gas. Fare riferimento alla retta di compressione. Da catalogo vengono forniti i valori F1 ed FR, quindi è facilmente calcolabile il valore F3 (massima estensione), la pendenza ed il valore di massima compressione. Stabilus © – LIFT-O-MAT Gas Spring
Per il valore di forza siamo partiti da un valore di F1 = 100N per i pistoni laterale e 150N per il centrale con una compressione del 50%.
Abbiamo quindi calcolato le rigidezze risultanti e da una prima simulazione (descritta avanti) abbiamo visto come la F1 del pistone centrale risultasse troppo elevata.
Abbiamo ripetuto quindi gli stessi passaggi scendendo fino a 100N (per il modello Inox Line si va da 100N a 600N con incrementi di 25N) ma il valore risultava ancora elevato. Quindi siamo passati alla versione classica che ci permette di avere una F1=50N. Abbiamo allora ripetuto tutti i calcoli comprese le simulazioni con questi nuovi valori.
Successivamente abbiamo verificato la compressione massima fornita dal catalogo di 150mm per il centrale e di 220mm.
Qui abbiamo condotto ulteriori verifiche di cui parliamo avanti.
Scelta delle dimensioni e disegno dei componenti
Tramite il codice MATLAB © abbiamo ottenuto una stima dei punti di attacco, le inclinazioni e la lunghezza dei pistoni e abbiamo preparato una prima bozza in SOLIDWORKS ©, molto schematica, tale da darci una prima visualizzazione grafica della pedana e permetterci di rilevare ulteriori misure più velocemente. (Vedi Fig. 10) Ovviamente il salto tra i due passaggi non è stato così diretto ma più volte siamo dovuti passare da un software all’altro per ottimizzare il tutto ed arrivare ad un buon compromesso tra le dimensioni contenute ma tali da rendere stabile il dispositivo, utilizzo di pistoni simili e con valori da catalogo, comodità dell’utilizzatore.

Fig. 10 – Prima bozza schematica realizzata a partire dai dati ottenuti tramite il codice MATLAB © con il fine di manipolare meglio le geometrie e avere dei riferimenti più concreti.

Successivamente siamo passati ad un disegno più accurato di pedana, braccio di supporto e base in modo da valutare anche le rotazioni e poi poter passare a delle simulazioni vere e proprie.
Il giunto sferico
Per la creazione del giunto abbiamo bisogno di diverse parti: la pedana, una sfera, un cappuccio e poi il perno che si collega al braccio di supporto. Nella pedana è previsto un foro a forma di calotta sferica che accoglierà la sfera che a sua volta sarà bloccata dal cappuccio. Dal foro modellato sul cappuccio (di cui parleremo in seguito) potremo garantire la connessione tra perno e sfera. Una volta vincolati perno e sfera il giunto sarà funzionante. Difatti la sfera è libera di ruotare (ma non di traslare) intorno al suo centro geometrico fino a quando il perno non arriva a battuta con il bordo del cappuccio modellato ad hoc.
Ovviamente la sfera richiederà un materiale resistente come un acciaio al cromo e una superficie liscia.

La pedana
La pedana si basa su un rettangolo di dimensioni 200x120cm tale da lasciare libere le dita e sono stati inserite delle asole per poter far passare alcune cinte per il fissaggio del piede come suggerito nel brevetto. La pedana ha uno spessore di 6mm (Fig. 11).
È stato poi aggiunto un supporto per il tallone.
Dopo le ulteriori valutazioni geometriche sono stati aggiunti 3 tacchetti su cui praticare i fori per i perni dei pistoni. I fori per i pistoni laterali sono perpendicolari alla pedana mentre per il pistone centrale è stato necessario inclinarlo (vedi discussione sui perni dei pistoni). Fig. 13

Fig. 11 - Geometria di partenza per la pedana

Un’ulteriore aggiunta è stata fatta creando la sede per la sfera del giunto sferico con i fori per le viti della copertura di fissaggio.
Sono stati poi aggiunti alcuni dettagli estetici come sformature e raccordi.
Globalmente ha un peso di 1,428 kg con un baricentro sull’asse di simmetria e spostato di 74,64 mm dal centro del giunto sferico, nella direzione del piede.
È stata anche valutata la possibilità di asportare del materiale dalla parte inferiore al fine di renderla più leggera ma ciò non è stato necessario in quanto questo peso aggiuntivo ci consentiva di stabilizzare meglio la posizione di riposo.

È stato anche aggiunto un foglio di materiale polimerico rigido dallo spessore di 1,5mm sulla superficie al fine di rendere più confortevole la pedana, migliorare l’adesione e limitare la sensazione di freddo provata a contatto con materiali metallici. Il materiale polimerico risulterà inoltre resistente agli attacchi chimici che un oggetto del genere può subire: chiaramente durante la vita del prodotto sarà necessario disinfettare adeguatamente la superficie, soprattutto nel caso questo oggetto sia presente in uno studio specializzato di riabilitazione. Tale superficie polimerica è pensata anche per resistere ai disinfettanti. Un possibile candidato è il polipropilene, polimero termoplastico che oltre alla bassa densità vanta una buona resistenza termica e all’abrasione, inoltre è riciclabile.

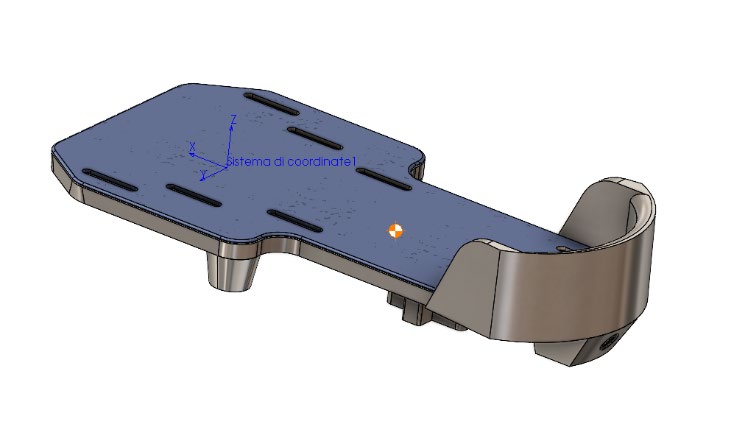
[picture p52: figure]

Fig. 12 – Pedana completa con la copertura superficiale in materiale polimerico. Presente anche il sistema di riferimento solidale alla pedana e il centro di massa.

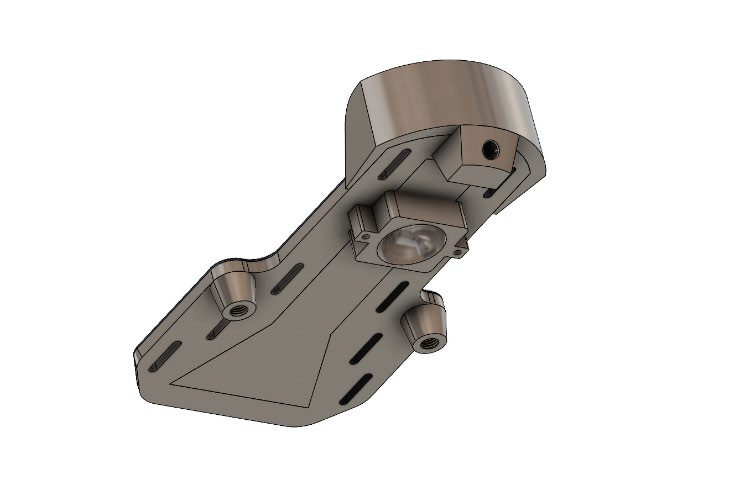
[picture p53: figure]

Fig. 13 – Vista inferiore della pedana. Si vedono i tacchetti per i fori, la sede per il giunto sferico e la forma generale valutata come ipotesi per eliminare del materiale qualora fosse risultato necessario.

Infine è stata aggiunta la porzione che si collega al giunto sferico tramite una estrusione seguita da un taglio in rivoluzione per creare il foro che accoglierà la sfera.
Il braccio di supporto
Per la modellazione del braccio di supporto dopo vari tentativi, cercando di combinare in vario modo delle estrusioni e delle geometrie di rivoluzioni per seguire la forma fornita dal brevetto abbiamo notato che il brevetto si riferisce alla forma del braccio di supporto come “wishbone” che indica la forcula, osso presente negli uccelli. Questo ci ha fornito uno spunto per pensare a una forma meno appuntita. Ci siamo quindi affidati a delle geometrie di loft, che sicuramente creano forme più sinuose.
Affidandoci alle misure fornitoci dal programma MATLAB © sviluppato, ragionando per simmetria, abbiamo fissato nello spazio due punti da cui abbiamo imposto una estrusione che poi si sarebbero collegate tra loro tramite le geometrie di loft (con aggiunta di vincoli di inizio e di fine per ridurre al minimo il numero di spigoli). Successivamente abbiamo introdotto un perno a cui si sarebbe collegata la sfera del giunto sferico, l’inclinazione è stata pensata da poter essere ortogonale alla pedana in condizioni di riposo.

Fig. 14 - Primo prototipo “wishbone” per il braccio di supporto

Questa geometria presenta un problema: la forma è tale da andare facilmente a battuta con i pistoni laterali, soprattutto nei movimenti di rotazione esterna/interna.

Dopo diversi tentativi di rimodellamento e misurazioni ci siamo ingegnati per evitare calcoli articolati sviluppando una nuova geometria, che chiameremo “Geometria ad Y”.
Questa versione combina la forma della forcula con la necessità di evitare il contatto tra il pezzo e i pistoni, la novità sta quindi in questa nuova estremità più longilinea che parte dal braccio per collegarsi alla pedana. L’ultima versione (Fig. 15) è considerata come formata da diversi segmenti cilindrici cavi cosi da diminuire il peso complessivo e fornire anche una maggiore resistenza meccanica. Inoltre questa struttura è anche più facilmente realizzabile.

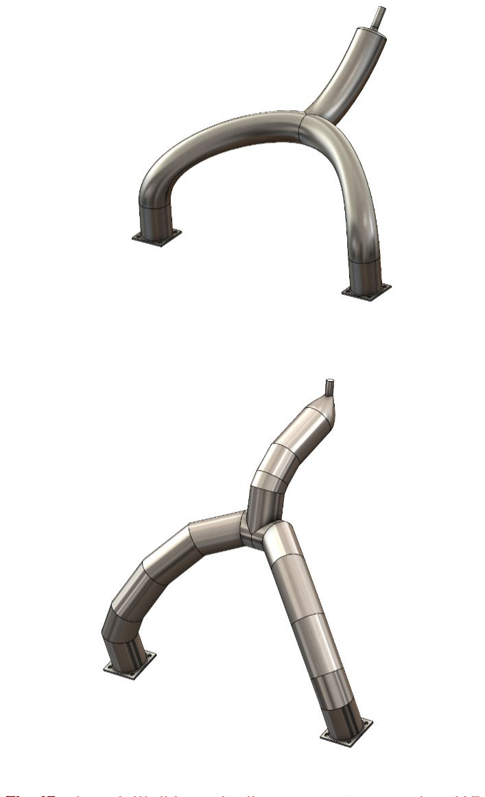
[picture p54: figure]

Fig. 15 - I modelli di braccio di supporto “geometria ad Y”. Sopra una bozza e sotto il modello definitivo.

Alle estremità che si ancorano alla base sono state progettate delle piastre con fori per viti M4, di distanze 39x39mm.

La base
La base è stata probabilmente il pezzo che ha subito più modifiche dal modello originale, inoltre è sicuramente quello con più versioni. Abbiamo provato con la forma a trapezio forato come da modello, abbiamo provato una forma a V rovesciata e ne abbiamo pensate diverse altre.

Fig. 16 – Foto dei primi prototipi per la base
La versione che presentiamo ha una peculiare forma ad H con braccia di diversa lunghezza, ciò permette di fornire gli stessi identici ancoraggi delle altre versioni, risparmiando in volume. Un design che risparmia in volume risparmierà in massa.

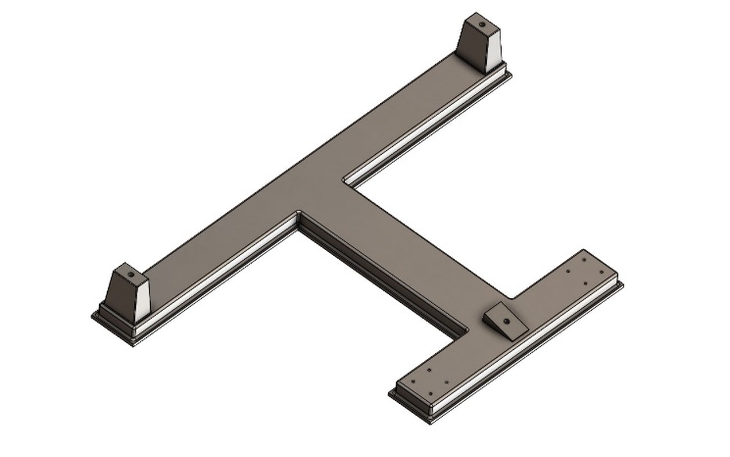
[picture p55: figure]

Fig. 17 – Modello della base con forma ad H
Chiaramente questo aspetto diventa fondamentale nella progettazione di un dispositivo medico che può essere spostato e manovrato all’interno di un locale adibito alla riabilitazione del paziente ma anche dal paziente stesso.
Le dimensioni dipendono dai risultati del programma da MATLAB © e dalla prima bozza che ci diranno a che distanza saranno gli ancoraggi dei pistoni e del braccio di supporto.

Il cappuccio (piastrina di accoppiamento) Per la creazione del cappuccio abbiamo cominciato dal creare una calotta sferica per poi aggiungere un’estrusione dal piano dove si appoggia la calotta stessa per poter applicare i fori che fisseranno il tutto alla pedana.
In seguito abbiamo dovuto modellare il foro che avrebbe dovuto contenere il movimento della sfera e quindi di tutto il sistema. Per farlo abbiamo ripreso le misure degli angoli ai limiti articolari del piede e, immaginando la normale al piano di estrusione come la posizione del perno in condizione di riposo, abbiamo disegnato delle rette che originano nel centro di rivoluzione e formano gli angoli che forma il piede ai limiti articolari in caso di flessione e nel caso di eversione/inversione.
Queste rette saranno gli assi dei cilindri che taglieranno la superficie della calotta, in questo modo ci è possibile di identificare visivamente la posizione del perno ai limiti articolari tramite dei fori nella calotta
Nel caso di rotazione non è stato necessario in quanto il movimento avviene intorno all’asse ortogonale alla pedana che per come abbiamo scelto la condizione di riposo si trova parallelo al perno che collega al braccio di supporto.
Successivamente, disegnata e specchiata una spline sul piano di lavoro affinché contornasse i fori citati in precedenza, abbiamo provveduto a sfruttare un taglio estruso per completare il pezzo.
Per modellare la spline ci siamo ispirati alle immagini fornite dal brevetto che sono tali da indirizzare il piede nelle rotazioni solo degli assi principali.
Come altra opzione abbiamo sviluppato un altro cappuccio da sostituire con la peculiarità che permette movimenti composti (e.g. flessione fino al limite articolare + eversione).
Questa modifica potrebbe permettere una riabilitazione più differenziata per il paziente.

Fig. 18 – Immagine del cappuccio terminata la prima modellazione

La descrizione seguente fa riferimento al progetto nella versione utilizzata per la simulazione quindi con tutti i componenti correttamente dimensionati.
Abbiamo utilizzato gli accoppiamenti per disporre la pedana con le inclinazioni desiderate procedendo prima per il pitch, roll e yaw e poi per le combinazioni di essi ovvero pitch+roll. Questa è l’unica combinazione che abbiamo considerato poiché le altre sono meno percettibili in quanto le due articolazioni della caviglia sono tali da limitare alcuni movimenti a seconda della loro disposizione relativa. Utilizzando quindi gli accoppiamenti per disporre correttamente la pedana in assieme abbiamo utilizzato la funzione di schizzo “curva di intersezione” per tracciare l’intersezione tra la copertura sferica e il perno di accoppiamento tra braccio di supporto e giunto sferico (Fig. 19 e Fig. 20). Abbiamo tracciato tutte le intersezioni per le inclinazioni di interesse, soltanto da un lato rispetto l’asse di simmetria, e poi le abbiamo proiettate su uno schizzo parallelo alla piastrina di accoppiamento.
Successivamente abbiamo ottenuto una linea curva unendo questi percorsi che poi abbiamo specchiato ottenendo un percorso chiuso dal quale abbiamo fatto un’estrusione rispetto il piano (Fig. 21).
All’estrusione abbiamo dato anche un certo grado di sformatura in modo da rendere il taglio meno netto.

Successivamente abbiamo nuovamente verificato, per le stesse posizioni considerate per le curve di intersezione, che non vi fosse compenetrazione con lo strumento “Rilevamento interferenze”.

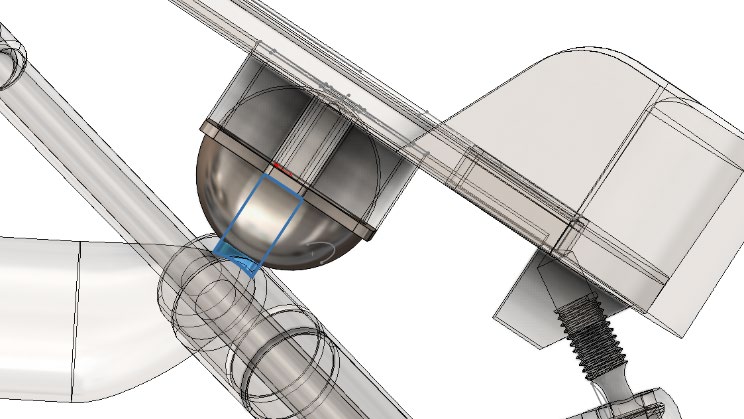
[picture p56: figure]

Fig. 19 – Intersezione tra la copertura sferica e il perno di accoppiamento nella posizione di riposo (pedana a 30° rispetto l’orizzontale).

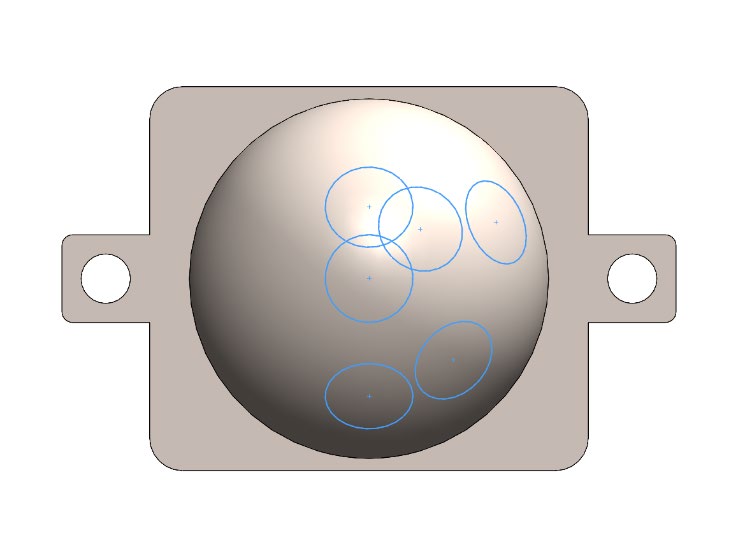
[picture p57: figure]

Fig. 20 - Vista parallela alla piastrina di accoppiamento dello schizzo 3D delle varie curve di intersezione

Fig. 21 – Vista perpendicolare parallela alla piastrina di accoppiamento.

I pistoni
Per i pistoni abbiamo utilizzato il file CAD fornito direttamente da Stabilus © a cui abbiamo dovuto fare alcune modifiche, sia funzionali, per permettere il corretto scorrimento tra tubo e stelo e per il giunto sferico, sia per le far sì che le dimensioni fossero esattamente quelle del catalogo (Fig. 23 e Fig. 24).
Su questi valori abbiamo condotto diverse verifiche: per ogni movimento necessario abbiamo controllato sia che non vi fossero né una compressione né un’estensione maggiore di quella permessa. Questa verifica l’abbiamo condotta sia sulla bozza 3D (Fig.
10) che su un primo modello molto semplice (Fig. 22) tale da tener conto dell’effettivo movimento dei pistoni.
Successivamente (dopo il primo cambio tra Inox Line e la serie classica) abbiamo ripetuto le verifiche ma in una versione aggiornata dell’assieme.

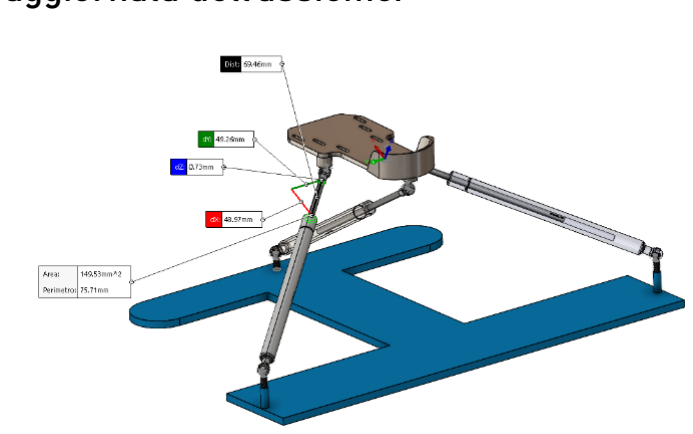
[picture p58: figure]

Fig. 22 – Assieme bozza utilizzato per fare diverse misure e verifiche
Per quanto riguarda il perno con la testa sferica di diametro 10mm è stato prima ricostruito rispettando le dimensioni da catalogo, quindi considerando un perno con filettatura M8x1,25 di 13 mm e un’altezza totale di 28 mm.

Fig. 23 – Pistone centrale modificato con le misure offerte dal catalogo Stabilus ©

Fig. 24 – Pistone laterale modificato con le misure offerte dal catalogo Stabilus ©.

I perni sono stati ripresi dopo aver completato il primo dimensionamento grossolano dei componenti per verificare consentissero effettivamente le rotazioni desiderate.
Abbiamo utilizzato una versione quasi ultimata dell’assieme (tutti i componenti nello stato finale a meno di quale dettaglio) e il controller accoppiamenti che ci ha permesso di disporre facilmente la pedana nelle angolazioni critiche in modo da verificare con lo strumento “rileva interferenze”.
È stato allora necessario sfinare il collo prima della testa in modo da aumentare la rotazione permessa. Particolare attenzione l’abbiamo posta sul perno collegante pistoni laterali e base inclinandolo di 54° rispetto la verticale. (Fig. 25)
Questo perno che nell’assieme utilizzato per le simulazioni risulta avvitato in realtà può ruotare liberamente (far riferimento al discorso finale).

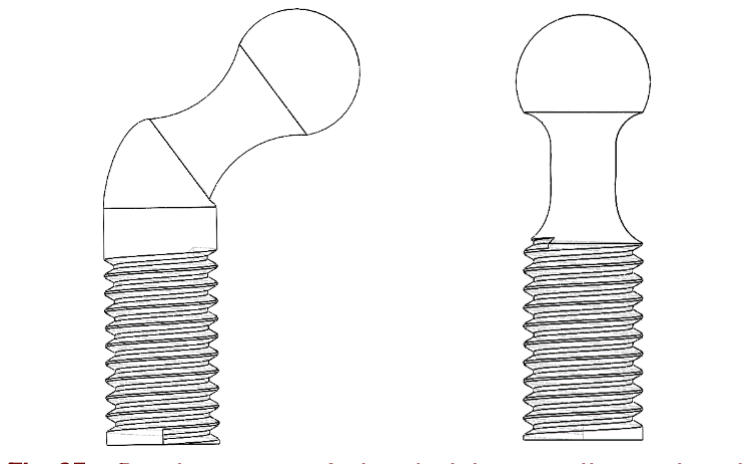
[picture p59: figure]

Fig. 25 – Perni con testa sferica. A sinistra quello tra pistoni laterali e base e a destra quello tra i pistoni e i restanti punti di collegamento.

E bene sottolineare che nella realtà risulta permesso un pitch di 3° minore di quello ipotizzato, per entrambe le direzioni. Questa limitazione e dovuta al pistone centrale e al suo perno che non abbiamo voluto sfinare ulteriormente in modo da garantire ancora una certa resistenza (Fig. 26).
Questo ci ha permesso di ottimizzare ulteriormente le dimensioni dei vari componenti e finalizzare alcune misure e dettagli lasciati indietro nei passaggi precedenti.

Fig. 26 – Compenetrazione nel giunto sferico a seguito di una flessione dorsale di 42° (valore massimo)

Materiali
Per il progetto è stato utilizzato un acciaio inossidabile AISI 316L [24] tale da mantenere la resistenza sia meccanica sia alla corrosione e tale da permettere una corretta sanificazione e pulizia del dispositivo. Questo acciaio presenta un’ottima scelta tra le ottime caratteristiche che ne fanno un materiale di punta del settore medicale e un costo relativamente basso.
Tuttavia, per un ulteriore risparmio si potrebbe utilizzare anche l’AISI 304L con caratteristiche simili ma un costo più contenuto [25, 26].
In ogni caso risulta più che appropriato un qualunque acciaio inossidabile di grado chirurgico [27, 28].

I pistoni sono rappresentati in acciaio inossidabile 316L e metallo con una copertura in plastica come indicato nel catalogo.
Altri componenti
Per il fissaggio del braccio di supporto sulla base sono state utilizzate delle viti M4 a testa svasata piana con cava esagonale mentre per il fissaggio della piastrina di accoppiamento delle viti M4 con testa a bottone a cava esagonale.
Le restanti filettature sono M8x1,25
Sono state effettuate anche delle modifiche ulteriori sulla base ed alcuni elementi collegati ad essa di cui parliamo più avanti.

## Simulazioni

Le simulazioni sono state effettuate mediante il pacchetto aggiuntivo “SOLIDWORKS MOTION”.
È stata considerata la gravità terrestre e i componenti costituiti in acciaio AISI 316L.
È stato considerato il peso agente della gamba poggiata sulla pedana come una forza pari a 58,.86 N (misura sperimentale) applicata a 30mm dall’origine nel piano xy lungo la simmetria.
Le simulazioni hanno tutte una durata di 5 secondi.
Abbiamo considerato il contatto (steel dry-steel dry) tra piastrina di accoppiamento e il perno del braccio di supporto. Non sono state considerate le coppie sferiche di pistoni e perni in quanto avevamo già effettuato una verifica delle possibili angolazioni e di compenetrazioni ai limiti articolari, quindi abbiamo lasciato solamente l’accoppiamento di concentricità.
Il comportamento dei pistoni è stato modellato in simulazione considerando una forza sulla superficie dello stelo pari a FF! + FFRR e una molla elastica di costante adeguata

e un coefficiente di smorzamento pari a 1 N/mm s. (Fig. 27 e Fig. 28)

La costante elastica è stata ricavata mediante il già citato codice MATLAB ©, ovvero 136.36 N/m per i pistoni laterali e 166.66 N/m per il pistone centrale (questo valore è quello a cui siamo arrivati dopo le considerazioni seguenti).
Una prima simulazione è stata effettuata nella condizione di riposo e ci ha portato a identificare un problema nei pistoni che ci ha costretto a passare dalla serie Inox Line alla serie classica poiché risultava necessaria una forza F1 inferiore per il pistone centrale. Questa simulazione è stata eseguita con la stessa logica delle seguenti ma lo spostamento risultava fortemente vincolato alla resistenza del pistone centrale.
Quindi abbiamo abbassato il valore di F1 a 50N arrivando così al modello finale utilizzato per le simulazioni e gli ulteriori controlli per accoppiamenti e compenetrazioni.

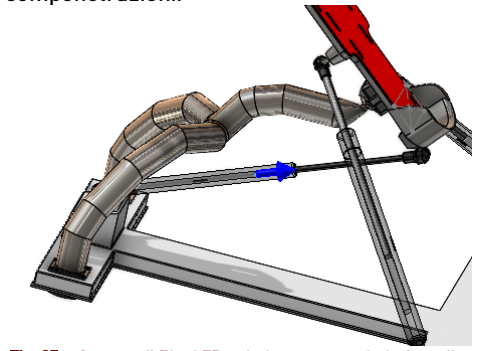
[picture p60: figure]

Fig. 27 – Somma di F1 ed FR sul pistone centrale in fase di simulazione

Fig. 28 – Molla elastica sul pistone centrale in fase di simulazione
Tutte le simulazioni citate sono state effettuate più volte tra le varie versioni di assieme ma i risultati seguenti fanno riferimento al modello finale.

Lo scopo di queste simulazioni è quello di verificare che le forze/coppie necessarie per portare la piattaforma ai limiti articolari fossero ben lontane dai carichi massimi misurati e che quindi consentissero un corretto uso riabilitativo del dispositivo nel rispetto delle considerazioni fatte nel trattare la cinematica della caviglia, allora abbiamo considerato i movimenti in Flessione
Per la rotazione di pitch è stato imposto un accoppiamento di coincidenza tra il piano sagittale della pedana e il piano xy dell’assieme tale da bloccare le altre due rotazioni.
Questa considerazione ci è sembrata opportuna viste le condizioni di simmetria ed è stata utile per limitare problemi dovuti al solutore nel caso in cui la pedana deviasse leggermente dalla posizione esattamente centrale, situazione che nella realtà verrebbe bilanciata da un minimo lavoro del piede.

Abbiamo quindi diviso la flessione in plantare e dorsale.
Per la flessione plantare abbiamo applicato una forza pari a 55,35 N, perpendicolare alla pedana, sul piano di simmetria e a 120mm dall’origine.
Dalla simulazione è risultato uno spostamento massimo di 23° che rientra nei

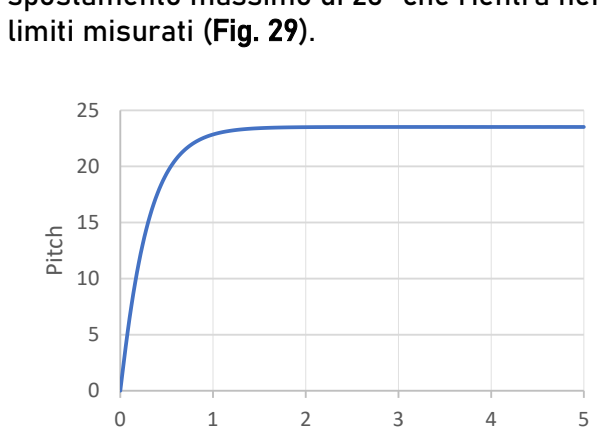
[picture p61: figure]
limiti misurati (Fig. 29).; Pitch

Fig. 29 – Angolo di Pitch per la flessione plantare

Per la flessione dorsale è stata imposta una forza di 83,63 N, applicata nello stesso punto ma nella direzione opposta.
Dalla simulazione risulta un angolo massimo di inclinazione di 42° (Fig. 31).

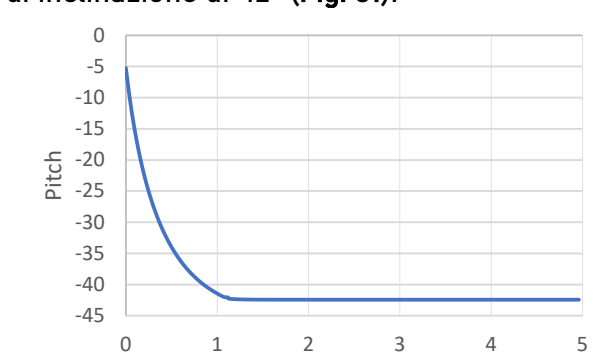
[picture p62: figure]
Pitch

Fig. 31 – Angolo di pitch per la flessione dorsale

Rotazione
Per la rotazione abbiamo considerato la piattaforma vincolata al piano xy (inclinazione di 30° rispetto il telaio, quindi situazione di riposo).
Per la rotazione abbiamo considerato entrambi i casi e già la forza minore ci portava al limite articolare.
Quindi la simulazione seguente è stata effettuata con una forza di 90,59 N applicata nello stesso punto della flessione ma con direzione parallela ad y.
La simulazione ha quindi restituito un angolo di 63° (Fig. 32).

Fig. 30 – In figura è riportato l’assieme principale utilizzato per le simulazioni (con meno dettagli della bozza finale). Nella colonna centrale le posizioni di riposo e nelle colonne laterali le posizioni ai limiti articolari.

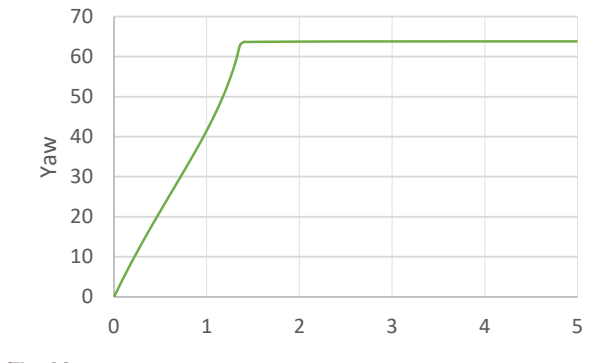
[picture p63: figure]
Yaw

Fig. 32 – Angolo di yaw per la rotazione

Eversione/inversione
Abbiamo considerato la pedana vincolata al piano coronale per considerazioni già fatte. Anche per questo movimento abbiamo visto come la forza minore fosse sufficiente ad arrivare al limite articolare quindi la simulazione seguente è stata effettuata con una forza di 33,45 N applicata sul piano della pedana ad una distanza di 120mm dall’asse y

Abbiamo quindi verificato un’inclinazione di

Fig. 33 – Angolo di roll per l’eversione

Sulla base di questi risultati e delle misure sperimentali possiamo dire che il dispositivo permette al piede di arrivare correttamente ai limiti articolari per i movimenti cercati.

Al fine di ottenere un ulteriore riscontro abbiamo effettuato altre simulazioni.
Pitch + roll
Abbiamo considerato un ulteriore movimento composto da una eversione/inversione e una flessione plantare (Fig. 34) e dorsale (non riportato nella relazione).
Ci è sembrato opportuno considerare questo movimento in quanto se il piede si muove lungo il piano sagittale il rapporto tra l’articolazione talocrurale e subtalare è tale da permettere movimenti più ampi rispetto la

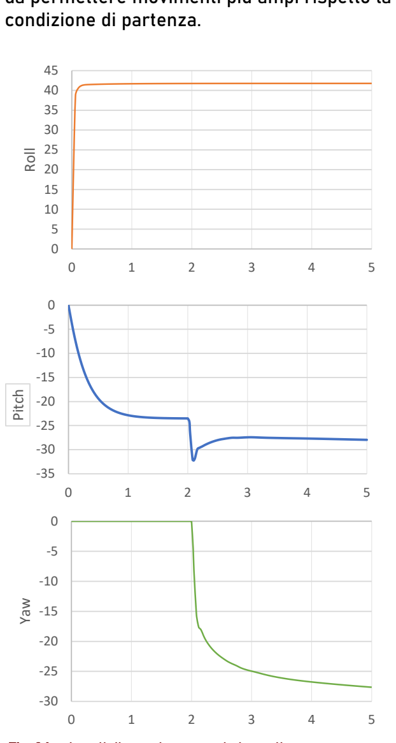
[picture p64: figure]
condizione di partenza.; Roll; Pitch; Yaw

Fig. 34 – Angoli di rotazione per pitch + roll

Un’ulteriore conferma
Abbiamo fatto un’ulteriore prova invertendo il ragionamento: abbiamo imposto gli angoli e misurato la coppia necessaria a produrre un tale spostamento (da Fig. 35 a Fig. 38)
I grafici seguenti esprimono la coppia in Nm.

Fig. 35 – Coppia del motore necessaria ad imporre uno spostamento di flessione plantare pari a quello misurato

sperimentalmente

Fig. 36 - Coppia del motore necessaria ad imporre uno spostamento di flessione dorsale pari a quello misurato sperimentalmente

Fig. 37 - Coppia del motore necessaria ad imporre uno spostamento di yaw pari a quello misurato

Fig. 38 - Coppia del motore necessaria ad imporre uno spostamento di roll pari a quello misurato sperimentalmente

Spostamento per punti
Avendo già i dati dell’’inclinometro abbiamo fatto ulteriori simulazioni considerando sempre un motore ma con spostamento definito per punti.
Anche qui abbiamo considerato due classi diverse.
Una prima classe di controllo l’abbiamo ottenuta imponendo uno spostamento per punti con il seguente schema: riposo → massimo → riposo → massimo (direzione opposta) →riposo.
Per la seconda classe abbiamo invece considerato i dati sperimentali dell’inclinometro selezionando i valori in modo tale da avere 50 punti su 5 secondi di simulazione.
I punti sono stati interpolati con l’interpolazione lineare.
Entrambe le classi le abbiamo simulate per

tutte e tre le rotazioni.; Coppia; Yaw

Fig. 39 – Coppia simulata del motore per la classe 1

Fig. 40 – Spostamento imposto dal motore per la classe 1

0

1

2

3

4

5

6

0 | 1 | 2 | 3 | 4 | 5

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
0 | 1 | 2 | 3 | 4 | 5

Coppia; Yaw

Fig. 41 - Coppia simulata del motore per la classe 2

Fig. 42 - Spostamento imposto dal motore per la classe 2

Condizione di riposo
Oltre le varie e ripetute simulazioni utilizzate per ottimizzare il dimensionamento dei pistoni abbiamo ripetuto una prova nella condizione di riposo (pedana a 30° rispetto il terreno) anche nell’assieme finale utilizzato per la presentazione.
Anche qui i risultati mostrano soltanto una leggerissima deviazione dalla posizione ipotizzata.

## Dettagli

Particolare attenzione è stata posta anche nel rifinire alcuni dettagli estetici e funzionali.
Si può notare come in corrispondenza di diversi punti del modello siano presenti degli accordi che creano una continuità più piacevole agli occhi rispetto al classico spigolo vivo. Inoltre questa riduzione del numero di spigoli vivi è anche un vantaggio del materiale usato in quanto questi spigoli possono facilitare l’insorgere dei processi di frattura soprattutto in condizioni di carico ciclico come nel nostro modello.
Nella fase finale del progetto è stata modificata in maniera significativa la base: tramite dei processi di estrusione abbiamo rimodellato l’interno della base affinché alcune parti fossero svuotate (in modo tale da alleggerire il pezzo), mentre altre risultassero piene, così da garantire solidità dove necessario, ad esempio in corrispondenza della serie di fori che accolgono le viti che stringono il braccio di supporto.
In tal modo il prototipo richiama una lamiera spessa 3 mm formata propriamente.

Fig. 43 – Vista in sezione del modello finale della base
Un’altra innovazione relativa alla base è stata la modifica degli ancoraggi dei pistoni laterali alla base stessa. Il sistema di semplice inserzione della vite nella base può risultare efficacie in ambiente CAD per le prime simulazioni, però nella realtà tale sistema risulta inadeguato. Per sopperire a questa mancanza abbiamo fatto della base un assieme più complesso: in corrispondenza degli ancoraggi abbiamo sviluppato un sistema costituito da un terminale collegato con cuscinetto a sfera libero di ruotare.
Il cuscinetto è quindi da considerarsi incastrato nel foro circolare cioè solidale alla base.
Inoltre, i fori sono stati inclinati in modo tale da favorire il gioco tra perno di ancoraggio e pistone. Il sistema descritto è riportato in Fig. 44 e Fig. 45.
Per concludere, abbiamo progettato anche dei gommini che si trovano al di sotto della base: essendo in gomma questi permetteranno alla base di rimane salda durante la sessione di riabilitazione, ma eviteranno il contatto diretto della base con il pavimento.
Per questi ci siamo ispirati alla forma caratteristica che hanno alcune estremità di stampelle: tramite una geometria di rivoluzione abbiamo creato una serie di cerchi concentrici che mimassero la forma dei gommini delle stampelle, che risultano particolarmente efficaci. (Fig. 49)

Fig. 44 – Vista in trasparenza del sistema di ancoraggio per i pistoni laterali con un cuscinetto a sfera


Fig. 45 - Vista in sezione del sistema di ancoraggio per i pistoni laterali con un cuscinetto a sfera

## Conclusioni e possibili sviluppi

Dalle simulazioni è risultato che la forza esplicata dal piede è sufficiente a portare la piattaforma ai limiti articolari.
Il dispositivo è molto semplice e di dimensioni contenute, questo permette un utilizzo comodo sia in ambito domestico che all’interno di una clinica.

Il dispositivo rispetta la maggior parte delle linee guida per la riabilitazione e non eccede mettendo al primo posto la salute e del paziente eliminando la possibilità di produrre ulteriori infortuni.
Un possibile miglioramento potrebbe essere quello di utilizzare dei pistoni con attuatore che consentono di incrementare il carico passando da una prima fase di vera e propria riabilitazione fino ad arrivare ad un potenziamento vero e proprio dell’articolazione. Inoltre, questo permetterebbe di personalizzare ulteriormente il dispositivo per il singolo paziente ma renderebbe il tutto più costo e più difficile da utilizzare.
Inoltre è possibile osservare che il cappuccio risulta personalizzato sulla base dei limiti articolari del soggetto. Si potrebbe pensare di realizzare un cappuccio più permissivo e una mascherina aggiuntiva personalizzata per ogni singolo paziente e applicabile esternamente al cappuccio.

Si potrebbero anche realizzare alcuni componenti in leghe più leggere al fine di limitarne il peso ma si rischia di incorrere in un innalzamento dei costi cercando di mantenere la stessa resistenza e stabilità.

## Materiale supplementare

A fine documento sono riportate delle immagini aggiuntive del modello finale completo di tutte le considerazioni fatte. Nel materiale extra troviamo:
- Modello finale CAD nella cartella “Modello”
- Tutte le immagini inserite
- File di considerazioni sui pistoni estratto dal catalogo
- Brevetto citato
- Catalogo di riferimento
- Dati delle simulazioni sia in file .csv che il foglio di lavoro

- Simulazione finale su cui abbiamo effettuato tutti i test principali (simulazione 5)
- Vecchie versioni di progetto e/o simulazione nella cartella “Old”
- Bozza 3D di lavoro e codice MATLAB citati
- Dati grezzi e fogli di lavoro per l’inclinometro
- Foglio di lavoro con le forze misurate
- File di lavoro per la misura delle rotazioni
- Registra schermo delle simulazioni così da includere movimento e grafici

Tutto il materiale citato è possibile trovarlo nella pendrive e nel seguente archivio: https://bit.ly/bioprotesi

## Opere citate

[1] Hayden, «Ankle rehabilitation device - US Patent 6,277,057B1,» 2001.
[2] L. Chinn, «Rehabilitation of Ankle and Foot Injuries in Athletes,» Clinics in Sports Medicine, vol. 29, n. 1, pp. 157-167, 2010.
[3] Y.-N. Wu, «Combined Passive Stretching and Active Movement Rehabilitation of Lower-Limb Impairments in Children With Cerebral Palsy Using a Portable Robot,» [Online]. Available: https://doi.org/10.1177%2F1545968310388666.
[4] J. E. Deutsch, «Post-Stroke Rehabilitation with the Rutgers Ankle System,» [Online]. Available: https://doi.org/10.1162/1054746011470262.
[5] C. E. Syrseloudis, «Design of a Simple and Modular 2-DOF Ankle Physiotherapy Device Relying on a Hybrid Serial-Parallel Robotic Architecture,» Applied Bionics and Biomechanics , vol. 8, 2011.
[6] J. Weineck, «Anatomia sportiva,» in Principi di anatomia funzionale dello sport, Calzetti editori, 2003, pp. 181-193.
[7] D. Thompson, «Ankle (talocrural) joint,» [Online]. Available: https://ouhsc.edu/bserdac/dthompso/web/namics/ankle.htm.
[8] I. D. C. Racu, «An Overview on Ankle Rehabilitation Devices,» Advanced Materials Research, vol. 1036, pp. 781-786, 2014.
[9] W. R. Frontera, «Proprioception and Coordination,» in Rehabilitation of Sports Injuries: Scientific Basis, Blackwell Publishing, 2003, pp. 274-287.
[10] J. S. a. Z. T. a. N. C. Dai, «cite-key Sprained Ankle Physiotherapy Based Mechanism Synthesis and Stiffness Analysis of a Robotic Rehabilitation Device,» Autonomous Robots, vol. 16, n. 2, pp. 207--218, 2004.
[11] G. F. Harris, in Foot and Ankle Motion Analysis: Clinical Treatment and Technology (Biomedical Engineering), pp. 23-25, 473-487.
[12] C. L. Brockett, «Biomechanics of the ankle,» Orthop Trauma. , vol. Jun; 30(3), p. 232–238, 2016 .
[13] C. Racu, «Preliminary mathematical model of a new anklòe rehabilitation device,» Journal of Engineering Studies and Research, vol. 21, n. 2, pp. 78-84, 2015.
[14] T. Shimano, «Relationship between the number of repetitions and selected percentages of one repetition maximum in free weight exercise in trained and untrained men,» Journal of Strength and Conditioning Research, vol. 20(4), p. 819–823, 2006.
[15] E. Moraes, «Relationship between Repetitions and Selected Percentage of One Repetition Maximum in Trained and Untrained Adolescent Subjects,» Journal of Exercise Physiology, vol. 17, n. 2, 2014.
[16] W. S. Doss, «A comparison of concentric, eccentric, and isometric strength of elbow flexors».
[17] C. G. Mattacola, «Rehabilitation of the Ankle After Acute Sprain or Chronic Instability,» Journal of Athletic Training , vol. 37, n. 4, p. 413–429, 2002.
[18] «PS01 Electronic Balance Digital Fishing,» Dr. Meter, [Online]. Available: https://www.amazon.it/gp/product/B078KP5YGP/ref=ppx_yo_dt_b_search_asin_title?ie=UTF8&psc=1.
[19] Witmotion, «BWT901CL - 9 Axis IMU Sensor Angle Inclinometer + Acceleration + Gyro + Mag,» [Online]. Available: https://www.wit-motion.com/bluetooth-gyroscope/witmotion-bluetooth-2-0-mult-connect-bwt901cl-9-axis.html.
[20] M. J. Girone, «Rutgers Ankle orthopedic rehabilitation interface,» 1999.
[21] J. Yoon, «Reconfigurable ankle rehabilitation robot for various exercises,» Journal of Robotic Systems, vol. 22, n. S1, pp. S15-S33, 2006.
[22] A. Logan, «The foot and the ankle - Clinical Applications,» pp. 35-50.
[23] Stabilus, «LIFT-O-MAT Gas Spring,» [Online]. Available: https://www.stabilus.com/products/non-locking-gas-springs .
[24] Carpenter technology, «Biodur ® 316LS,» [Online]. Available: https://www.carpentertechnology.com/alloy-finder/Biodur-316LS.
[25] AZO Material, «Medical Applications of Stainless Steel 304 (UNS S30400),» [Online]. Available: https://www.azom.com/article.aspx?ArticleID=6641.
[26] MEPS International Ltd, «World Stainless Steel Price,» [Online]. Available: https://worldsteelprices.com/stainless-steel-prices/.
[27] N. M. Winters GL, Stainless Steels for Medical and Surgical Applications, 2003.
[28] Y. Murty, «Use of stainless steels in medical applications,» [Online]. Available: https://www.researchgate.net/publication/282819958_Use_of_stainless_steels_in_medical_applications.

## Indice delle figure

FIG. 1 – IMMAGINE TRATTA DIRETTAMENTE DAL BREVETTO US 6,227,057B1 [1] | 3
FIG. 2– SISTEMA DI RIFERIMENTO CONSIDERATO PER IL PIEDE DESTRO. LE TRE ROTAZIONI SONO STATE CLASSIFICATE RISPETTIVAMENTE COME YAW (Y)
INTORNO L’ASSE Z, ROLL (R) INTORNO L’ASSE X E PITCH (P) INTORNO L’ASSE Y | 4
FIG. 3 - SONO RAFFIGURATI I NORMALI MOVIMENTI DI ROTAZIONE DELL’ARTICOLAZIONE DELLA CAVIGLIA. L’EVERSIONE E L’INVERSIONE INDICATO COME (R) OVVERO LA ROTAZIONE INTORNO L’ASSE X. LA FLESSIONE PLANTARE E DORSALE INDICATO COME (P) OVVERO LA ROTAZIONE INTORNO L’ASSE Y. L’ABDUZIONE E L’ADDUZIONE SPESSO INDICATE COME ROTAZIONE MEDIALE E LATERALE INDICATE COME (Y) OVVERO LA ROTAZIONE INTORNO L’ASSE
Z | 4
FIG. 4 – RIABILITAZIONE FUNZIONALE PER LA CAVIGLIA | 5
FIG. 5 – ASSI DI ROTAZIONE DELLE ARTICOLAZIONI TALOCRURALE E SUBTALARE [7] | 5
FIG. 6 - MISURAZIONE IN SOLIDWORKS © DELLE ROTAZIONI NEL CASO DI FLESSIONE PLANTARE E DORSALE MEDIANTE LE RETTE PASSANTI PER I MARKER.6 TAB. 1 – COPPIE (NM) CALCOLATE CON LA MEDIA DELLE FORZE MISURATE E IL BRACCIO MISURATO RISPETTO IL PUNTO DOVE È STATA ANCORATA LA FASCIA
PER LE MISURE DELLE FORZE, TENENDO CONTO DELLA ROTAZIONE MEDIA | 7
FIG. 7 - DISTRIBUZIONE DELLE MISURE DELLE FORZE [NEWTON] EFFETTUATE NELLE 6 POSIZIONI LIMITE PER ENTRAMBI I PIEDI. LA CROCE EVIDENZIA LA
MEDIA, VALORE CHE È STATO CONSIDERATO NEL RESTO DELLA TRATTAZIONE | 7
FIG. 8 – SONO RIPORTATI GLI STRUMENTI DI MISURA (A) OVVERO IL DINAMOMETRO, L’INCLINOMETRO, LE FASCETTE IN TESSUTO E UN CAVO INESTENSIBILE. IN (B) LA RAPPRESENTAZIONE GENERALE DI COME SONO STATE PRESE LE MISURE, PRECISAMENTE IL CASO DI FLESSIONE PLANTARE, CON LA FASCETTA IN TESSUTO NON ESTENSIBILE UTILIZZATA PER LE MISURE DELLA FORZA E IN (C)Z LA FASCETTA ELASTICA CON L’INCLINOMETRO. LE MISURE OTTENUTE CON L’INCLINOMETRO EFFETTUANDO TRE ROTAZIONI CONSECUTIVE IN ENTRAMBI I VERSI PRIMA PER INVERSIONE ED EVERSIONE (D), POI FLESSIONE PLANTARE E DORSALE (E) E INFINE PER LA ROTAZIONE MEDIALE E LATERALE (F). IN ROSSO SONO RAPPRESENTATI I VALORI MASSIMI (E MINIMI)
OTTENUTI CALCOLANDO LA MEDIA TRA I MASSIMI (E MINIMI) OTTENUTI PER OGNUNA DELLE TRE ROTAZIONI NEI DUE PUNTI ESTREMALI | 8
TAB. 2 - ANGOLI DI MASSIMA ESCURSIONE MISURATI MEDIANTE SOLIDWORKS ©. SONO RIPORTATI I DATI SIA PER IL PIEDE DESTRO (DX) CHE SINISTRO (SX) PER LE TRE ROTAZIONI YAW (Y), ROLLO (R) E PITCH (P). I VALORI SONO RIPORTATI IN GRADI E APPROSSIMATI ALLA PRIMA CIFRA DECIMALE ..... 8 TAB. 3 – MEDIA APPROSSIMATA DEI VALORI DI ROTAZIONE TRA PIEDE DESTRO E SINISTRO. GLI ANGOLI SONO CONSIDERATI IN MODULO, PER IL SEGNO FAR
RIFERIMENTO AL MOVIMENTO E AL SISTEMA DI RIFERIMENTO | 8
FIG. 9 - LEGGE LINEARE PER LA MOLLA A GAS. FARE RIFERIMENTO ALLA RETTA DI COMPRESSIONE. DA CATALOGO VENGONO FORNITI I VALORI F1 ED FR, QUINDI È FACILMENTE CALCOLABILE IL VALORE F3 (MASSIMA ESTENSIONE), LA PENDENZA ED IL VALORE DI MASSIMA COMPRESSIONE. STABILUS © –
LIFT-O-MAT GAS SPRING | 10
FIG. 10 – PRIMA BOZZA SCHEMATICA REALIZZATA A PARTIRE DAI DATI OTTENUTI TRAMITE IL CODICE MATLAB © CON IL FINE DI MANIPOLARE MEGLIO LE
GEOMETRIE E AVERE DEI RIFERIMENTI PIÙ CONCRETI | 10
FIG. 11 - GEOMETRIA DI PARTENZA PER LA PEDANA | 11
FIG. 12 – PEDANA COMPLETA CON LA COPERTURA SUPERFICIALE IN MATERIALE POLIMERICO. PRESENTE ANCHE IL SISTEMA DI RIFERIMENTO SOLIDALE ALLA
PEDANA E IL CENTRO DI MASSA | 11
FIG. 13 – VISTA INFERIORE DELLA PEDANA. SI VEDONO I TACCHETTI PER I FORI, LA SEDE PER IL GIUNTO SFERICO E LA FORMA GENERALE VALUTATA COME
IPOTESI PER ELIMINARE DEL MATERIALE QUALORA FOSSE RISULTATO NECESSARIO | 11
FIG. 14 - PRIMO PROTOTIPO “WISHBONE” PER IL BRACCIO DI SUPPORTO | 12
FIG. 15 - I MODELLI DI BRACCIO DI SUPPORTO “GEOMETRIA AD Y”. SOPRA UNA BOZZA E SOTTO IL MODELLO DEFINITIVO | 12
FIG. 16 – FOTO DEI PRIMI PROTOTIPI PER LA BASE | 13
FIG. 17 – MODELLO DELLA BASE CON FORMA AD H | 13
FIG. 18 – IMMAGINE DEL CAPPUCCIO TERMINATA LA PRIMA MODELLAZIONE | 14
FIG. 19 – INTERSEZIONE TRA LA COPERTURA SFERICA E IL PERNO DI ACCOPPIAMENTO NELLA POSIZIONE DI RIPOSO (PEDANA A 30° RISPETTO
L’ORIZZONTALE) | 14
FIG. 20 - VISTA PARALLELA ALLA PIASTRINA DI ACCOPPIAMENTO DELLO SCHIZZO 3D DELLE VARIE CURVE DI INTERSEZIONE | 14
FIG. 21 – VISTA PERPENDICOLARE PARALLELA ALLA PIASTRINA DI ACCOPPIAMENTO | 14
FIG. 22 – ASSIEME BOZZA UTILIZZATO PER FARE DIVERSE MISURE E VERIFICHE | 15
FIG. 23 – PISTONE CENTRALE MODIFICATO CON LE MISURE OFFERTE DAL CATALOGO STABILUS © | 15
FIG. 24 – PISTONE LATERALE MODIFICATO CON LE MISURE OFFERTE DAL CATALOGO STABILUS © | 15
FIG. 25 – PERNI CON TESTA SFERICA. A SINISTRA QUELLO TRA PISTONI LATERALI E BASE E A DESTRA QUELLO TRA I PISTONI E I RESTANTI PUNTI DI
COLLEGAMENTO | 15
FIG. 26 – COMPENETRAZIONE NEL GIUNTO SFERICO A SEGUITO DI UNA FLESSIONE DORSALE DI 42° (VALORE MASSIMO) | 16
FIG. 27 – SOMMA DI F1 ED FR SUL PISTONE CENTRALE IN FASE DI SIMULAZIONE | 17
FIG. 28 – MOLLA ELASTICA SUL PISTONE CENTRALE IN FASE DI SIMULAZIONE | 17
FIG. 29 – ANGOLO DI PITCH PER LA FLESSIONE PLANTARE | 17
FIG. 30 – IN FIGURA È RIPORTATO L’ASSIEME PRINCIPALE UTILIZZATO PER LE SIMULAZIONI. NELLA COLONNA CENTRALE LE POSIZIONI DI RIPOSO E NELLE
COLONNE LATERALI LE POSIZIONI AI LIMITI ARTICOLARI | 18
FIG. 31 – ANGOLO DI PITCH PER LA FLESSIONE DORSALE | 18
FIG. 32 – ANGOLO DI YAW PER LA ROTAZIONE | 19
FIG. 33 – ANGOLO DI ROLL PER L’EVERSIONE | 19

FIG. 34 – ANGOLI DI ROTAZIONE PER PITCH + ROLL | 19
FIG. 35 – COPPIA DEL MOTORE NECESSARIA AD IMPORRE UNO SPOSTAMENTO DI FLESSIONE PLANTARE PARI A QUELLO MISURATO SPERIMENTALMENTE .. 20 FIG. 36 - COPPIA DEL MOTORE NECESSARIA AD IMPORRE UNO SPOSTAMENTO DI FLESSIONE DORSALE PARI A QUELLO MISURATO SPERIMENTALMENTE..... 20
FIG. 37 - COPPIA DEL MOTORE NECESSARIA AD IMPORRE UNO SPOSTAMENTO DI YAW PARI A QUELLO MISURATO SPERIMENTALMENTE | 20
FIG. 38 - COPPIA DEL MOTORE NECESSARIA AD IMPORRE UNO SPOSTAMENTO DI ROLL PARI A QUELLO MISURATO SPERIMENTALMENTE | 20
FIG. 39 – COPPIA SIMULATA DEL MOTORE PER LA CLASSE 1 | 20
FIG. 40 – SPOSTAMENTO IMPOSTO DAL MOTORE PER LA CLASSE 1 | 20
FIG. 41 - COPPIA SIMULATA DEL MOTORE PER LA CLASSE 2 | 21
FIG. 42 - SPOSTAMENTO IMPOSTO DAL MOTORE PER LA CLASSE 2 | 21
FIG. 43 – VISTA IN SEZIONE DEL MODELLO FINALE DELLA BASE | 21
FIG. 44 – VISTA IN TRASPARENZA DEL SISTEMA DI ANCORAGGIO PER I PISTONI LATERALI CON UN CUSCINETTO A SFERA | 22
FIG. 45 - VISTA IN SEZIONE DEL SISTEMA DI ANCORAGGIO PER I PISTONI LATERALI CON UN CUSCINETTO A SFERA | 22
FIG. 46 - VISTA LATERALE | 27
FIG. 47 – VISTA FRONTALE | 27
FIG. 48 – VISTA SUPERIORE | 28
FIG. 49 – VISTA INFERIORE | 28
FIG. 50 – PARTICOLARE SULL’ESTREMITÀ DELLA BASE | 29
FIG. 51 – INGRANDIMENTO SUL GIUNTO | 29


Fig. 46 - Vista laterale

Fig. 47 – Vista frontale

Fig. 48 – Vista superiore

Fig. 49 – Vista inferiore


Fig. 50 – Particolare sull’estremità della base

Fig. 51 – Ingrandimento sul giunto

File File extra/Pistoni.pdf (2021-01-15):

CATALOGO; lmax; Ftl ) =; FILI =; - compressione %; Max


pg 34


Dal sito stabiliva .; sezione; Cad; • incrementi

Di VEDI LISTINO

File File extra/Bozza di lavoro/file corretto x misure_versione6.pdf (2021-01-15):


# Table of Contents

sbagliato L2=(abs(lxdx)+abs(lxc))*cosd(inclassez)+abs(((Lc-(1-allungamentocen-

clear all
close all
format short

# CALCOLO DIMENSIONI A RIPOSO

%%INSERIRE I DATI DI CATOLOGO E LA CONFIGURAZIONE DI RIPOSO (ANGOLI E %%ALLUNGAMENTO)

# CONFIGURRAZIONE CATALOGO

Lc=0.409;%lunghezza massima pistone centrale Ec=0.180; %escursione pistone centrale Lpdx=0.489; %lunghezza massima piste laterale Epdx=0.220; %escursione pistone laterale Fr=60; % vedi catalogo

# PIATTAFORMA:

z solidale alla tibia,a 30gradi da terra x punta avanti ocn le dita, y a sinistra

inclassez=30;
% origine centrato con la caviglia
%distanza dall'origine pistone di destra in cm lxdx=0.065;
lydx=-0.050;
lzdx=0;
%distanza dall'origine pistone di sx in cm lxsx=lxdx;
lysx=-lydx;
lzsx=0;
%distanza dall'origine pistone centrale in cm lxc=-0.04;
lyc=0;
lzc=0;

# PISTONI LATERALI

F1=100;
x=0.35;

allungamento=0.5; %allungamento pistone destra

% pistone destro
mFpdx=forza(Fr,F1,x,1-allungamento); %modulo

a=81; %angolo con l'asse z
b=45;% angolo tra x e la priezione del vettore su xy

Fpdxx=mFpdx*sind(a)*cosd(b); Fpdxy=mFpdx*sind(a)*sind(b);
Fpdxz=mFpdx*cos(a);

% pistone sinistro
mFpsx=forza(Fr,F1,x,1-allungamento); %modulo

gamma=a; %angolo con l'asse z
delta=-b;% angolo tra x e la priezione del vettore su xy

Fpsxx=mFpsx*sind(gamma)*cosd(delta); Fpsxy=mFpsx*sind(gamma)*sind(delta); Fpsxz=mFpsx*cos(gamma);

Fpdx=[Fpdxx Fpdxy Fpdxz];
Fpsx=[Fpsxx Fpsxy Fpsxz];
disp('Forza pistone di destra '), disp(Fpdx); disp('Forza pistone di sinistra '), disp(Fpsx);

# PISTONE CENTRALE

F12=250; %forza F12 dal catalogo xc=0.35;

allungamentocentrale=0.4; %l/l_0 centrlae

ac=-30; %angolo con l'asse z
bc=0;% angolo tra x e la proiezione del vettore su xy

mFpc=forza(Fr,F12,xc,allungamentocentrale); %modulo

Fpcx=mFpc*sind(ac)*cosd(bc); Fpcy=mFpc*sind(ac)*sind(bc);
Fpcz=mFpc*cosd(ac);
Fpc=[Fpcx Fpcy Fpcz];
disp('Forza pistone centrale '), disp(Fpc);

Forza pistone centrale
-122.5000 | 0 212.1762

# Equilibri

RX=Fpsx(:,1)+Fpdx(:,1)+Fpc(:,1); RY=Fpsx(:,2)+Fpdx(:,2)+Fpc(:,2); RZ=Fpsx(:,3)+Fpdx(:,3)+Fpc(:,3);

disp('Equilibrio a traslazione '), disp([RX RY RZ]);

%Bilancio dei momenti
%Mx=Fz*ly+Fy*lz
%My=Fx*lz+Fz*lx
%Mz=Fy*dx+Fx*ly

Mx=Fpsx(:,3)*lysx+Fpdx(:,3)*lydx+Fpc(:,3)*lyc-Fpsx(:,2)*lzsx-Fpdx(:,2)*lzdx-Fpc(:,2)*lzc; My=Fpsx(:,1)*lzsx+Fpdx(:,1)*lzdx+Fpc(:,1)*lzc-Fpsx(:,3)*lxsx-Fpdx(:,3)*lxdx-Fpc(:,3)*lxc; Mz=Fpsx(:,2)*lxsx+Fpdx(:,2)*lxdx+Fpc(:,2)*lxc-Fpsx(:,1)*lysx-Fpdx(:,1)*lydx-Fpc(:,1)*lyc;

disp('Equilibrio a rotazione '), disp([Mx My Mz]);

Equilibrio a traslazione
55.5923 | 0 410.2311

Equilibrio a rotazione
0 | -4.3865 | 0

# GEOMETRIE

Lc1=Lc-((1-allungamentocentrale)*Ec); H1=abs(Lc1*cosd(ac))*cosd(inclassez); Lp2=Lpdx-((1-allungamento)*Epdx); H2=abs(Lp2*(cosd(a))*cosd(inclassez));
H=max(H1,H2);
Hdiff=(max(H1,H2)-min(H1,H2))*cosd(inclassez); L=(2*abs(lydx))+2*max(abs(Lc1*sind(ac)*sind(bc)),abs(Lp2*sind(a)*sind(b)));

# sbagliato L2=(abs(lxdx)+abs(lxc))*cosd(inclassez)+abs(((Lc-(1-allungamentocentrale)*Ec))*sind(ac)*cosd(bc))+abs(((Lpdx-(1-al-

lungamento)*Epdx)*sind(a)*cosd(b)));

L22=+abs((Lp2*sind(a)*cosd(b)))-((abs(lxdx))); L21=+abs(Lc1*sind(ac)*cosd(bc))-(abs(lxc));

L2=L22+L21;
disp('Allungamento % pistoni laterali(IMPOSTO): '), disp(allungamento);
disp('Allungamento % pistone centrale(IMPOSTO): '), disp(allungamentocentrale);
disp('Altezza da terra in cm'), disp(H);
disp('Scarto in altezza'), disp(Hdiff);
disp('Larghezza totale max in cm'), disp(L); disp('Lunghezza totale in cm'), disp(L2/cosd(inclassez)); Lcf=Lc-(Ec*allungamentocentrale); Lpf=Lpdx-(Epdx*allungamento);
disp('Lunghezza pistone centrale'), disp(Lcf); disp('Lunghezza pistone laterale'), disp(Lpf);

Allungamento % pistoni laterali(IMPOSTO): 0.5000

Allungamento % pistone centrale(IMPOSTO): 0.4000

Altezza da terra in cm
0.2257

Scarto in altezza
0.1510

Larghezza totale max in cm 0.6294

Lunghezza totale in cm
0.3582

Lunghezza pistone centrale 0.3370

Lunghezza pistone laterale 0.3790

# ROTAZIONI

%VEDI ALTRO FILE
%nserire le rotazioni
%rotx=
%roty=
%rotz=
%riscrivere gli angoli ruotati %riscrivere tutto il codice

# CALCOLI

%prova a scrivere un sistema con 9 incognite %Equilibrio a rotazioen (3 eq)

% lx= per i pistoni laterali (1)
% lz=0 per tutti e tre (3 eq)
% lydx=-lysx pere i pistoni laterali (1)
% distanza y del pistone centrale è nulla
% %incognite
% syms Ldxx Ldxy Ldxz Lsxx Lsxy Lsxz Lcx Lcy Lcz
% eqn1=Fpsx(:,3)*Lsxy+Fpdx(:,3)*Ldxy+Fpc(:,3)*Lcy-Fpsx(:,2)*Lsxz-Fpdx(:,2)*Ldxz-Fpc(:,2)*Lcz==0;
% eqn2=Fpsx(:,1)*Lsxz+Fpdx(:,1)*Ldxz+Fpc(:,1)*Lcz-Fpsx(:,3)*Lsxx-Fpdx(:,3)*Ldxx-Fpc(:,3)*Lcx==0;
% eqn3=Fpsx(:,2)*Ldxx+Fpdx(:,2)*Ldxx+Fpc(:,2)*Lcx-Fpsx(:,1)*Lsxy-Fpdx(:,1)*Ldxy-Fpc(:,1)*Lcy==0;
% eqn4=Ldxx-Lsxx==0;
% eqn5=Ldxz==0;
% eqn6=Lsxz==0;
% eqn7=Lcz==0;
% eqn8=Ldxy+Lsxy==0;
% eqn9=Lcy==0;
% %X=[Ldxx Ldxy Ldxz Lsxx Lsxy Lsxz Lcx Lcy Lcz]
% [A,B] = equationsToMatrix([eqn1, eqn2, eqn3, eqn4, eqn5, eqn6, eqn6, eqn7, eqn8, eqn9], [Ldxx Ldxy Ldxz Lsxx Lsxy Lsxz Lcx Lcy Lcz])
% [V,S,U] = svd(A,0)
% % Verifica
% A=V*S*U'
% % Calcolo matrice pseudoinversa di A % pinvA=U*inv(S)*V'
% % Calcola soluzione
% X=pinvA*B

% syms Ldxy Ldxx Lcx
% eqn1=Fpsx(:,3)*Ldxy+Fpdx(:,3)*Ldxy==0;
% eqn2=Fpsx(:,3)*Ldxx-Fpdx(:,3)*Ldxx-Fpc(:,3)*Lcx==0;
% eqn3=Fpsx(:,2)*Ldxx+Fpdx(:,2)*Ldxx+Fpc(:,2)*Lcx+Fpsx(:,1)*Ldxy-Fpdx(:,1)*Ldxy==0;
% [A,B] = equationsToMatrix([eqn1, eqn2, eqn3], [Ldxy Ldxx Lcx ]) % x=linsolve(A,B)

function F=forza(Fr,Forzainizio,fattoreforze,allungamento)

F=Fr+Forzainizio+((Forzainizio)*(fattoreforze-1)*(allungamento)); end

Forza pistone di destra
89.0461 | 89.0461 | 99.0275

Forza pistone di sinistra
89.0461 -89.0461 99.0275

Published with MATLAB® R2020a

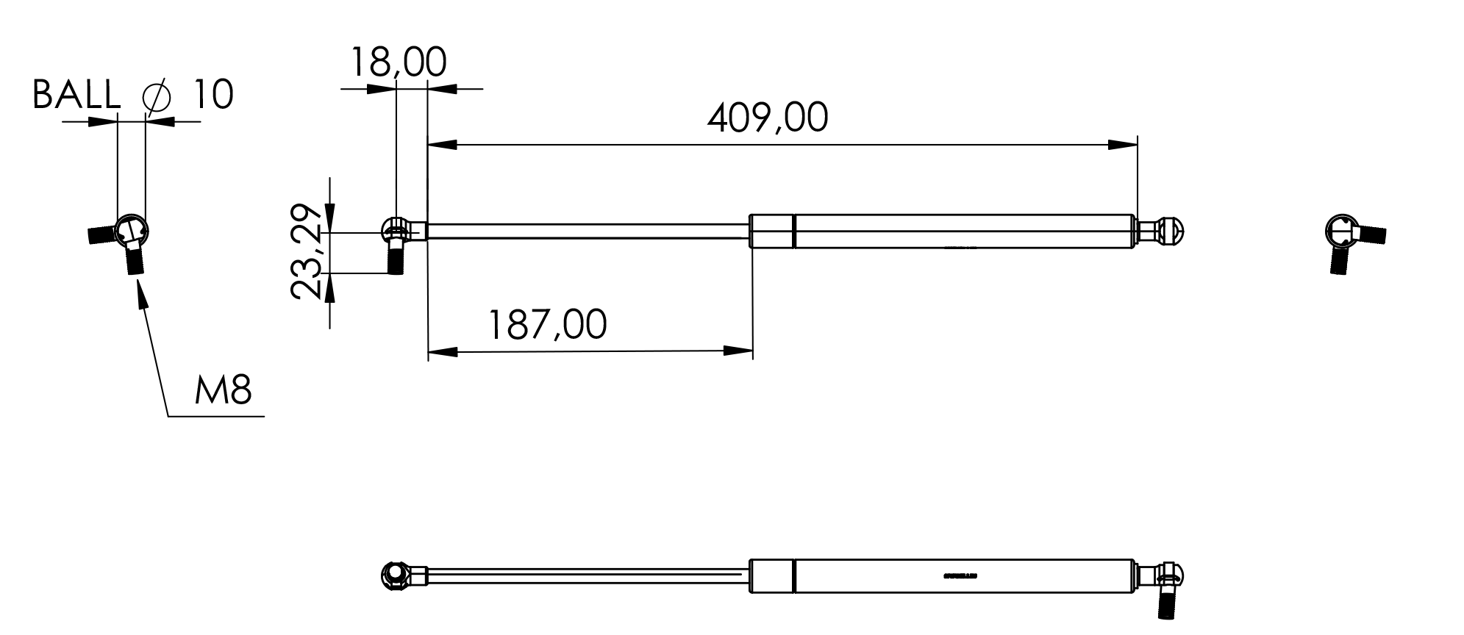
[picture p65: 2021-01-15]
File extra/File per relazione/pistonecentrale.png

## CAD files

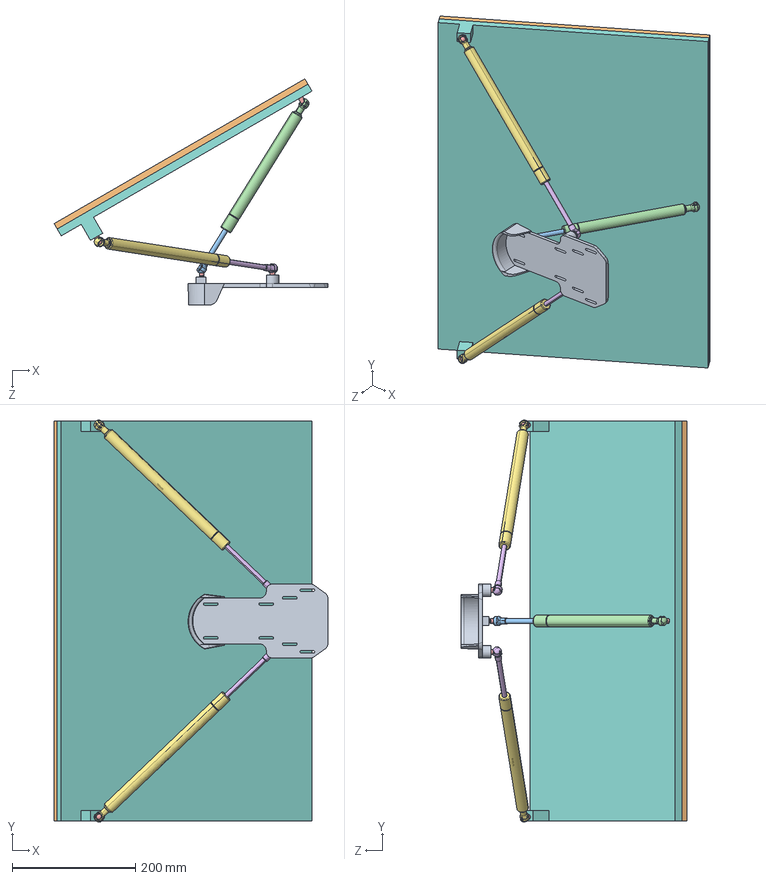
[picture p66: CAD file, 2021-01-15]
File extra/Bozza di lavoro/studio_movimento.SLDASM
444.3 x 652.5 x 367.4 mm
pedana
centrale_stelo
centrale_tubo
perno pistone centrale x 6
laterale_stelo x 2
laterale_tubo x 2
Parte1^studio_movimento

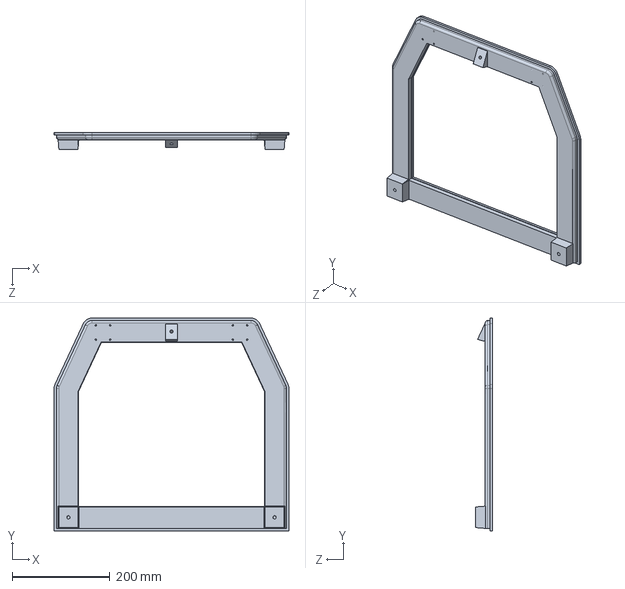
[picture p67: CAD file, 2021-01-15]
File extra/Simulazione 5/BaseAssieme_assemblaggio1.SLDPRT
480.0 x 435.0 x 35.0 mm

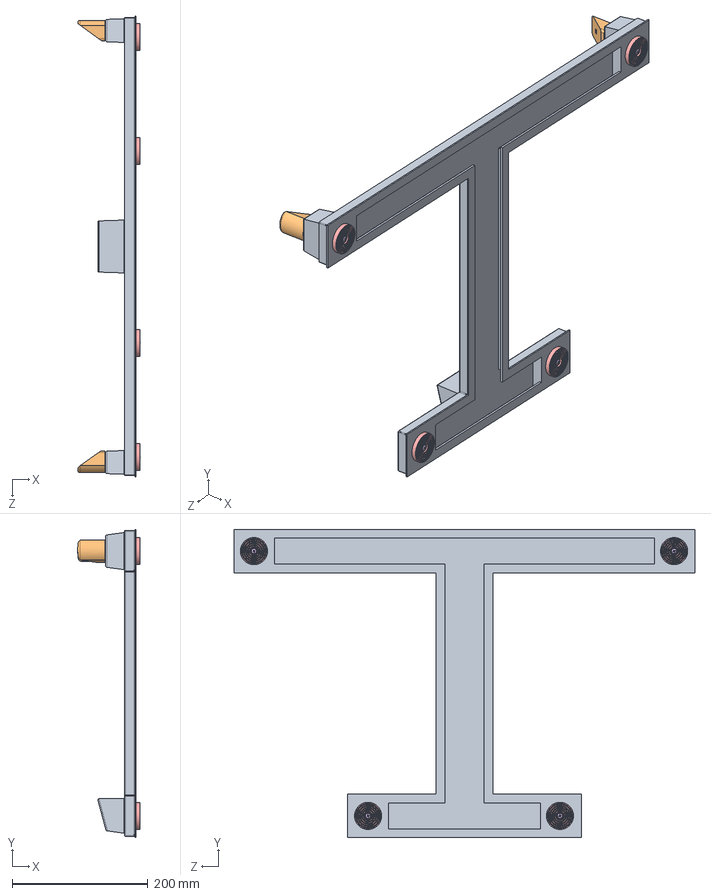
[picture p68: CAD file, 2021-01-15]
Modello/Base/assiemebase.SLDASM
92.1 x 454.0 x 679.0 mm
base2finale
ancoraggi x 2
instrument ball bearing_68_am x 2
prevailing torque hex nut_am x 2
gommini x 4
pan cross head_am x 4

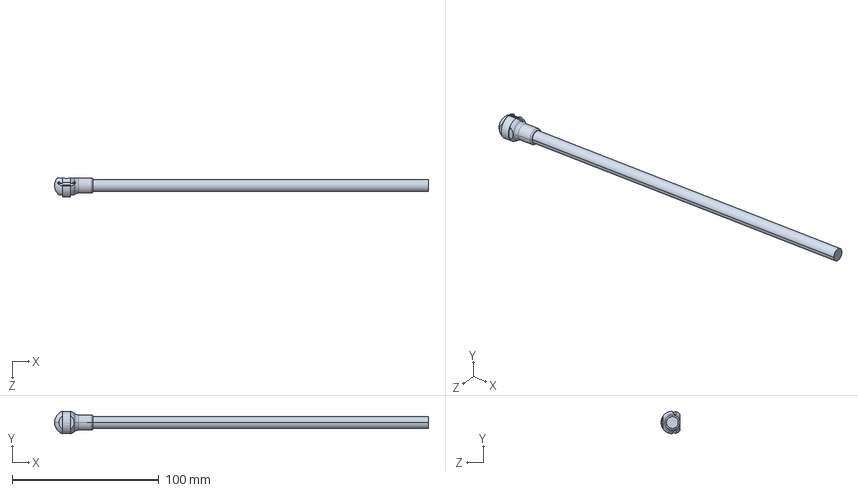
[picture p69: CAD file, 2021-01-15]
Modello/Pistoni/laterale_stelo_assemblaggio1.SLDPRT
254.7 x 15.5 x 13.0 mm

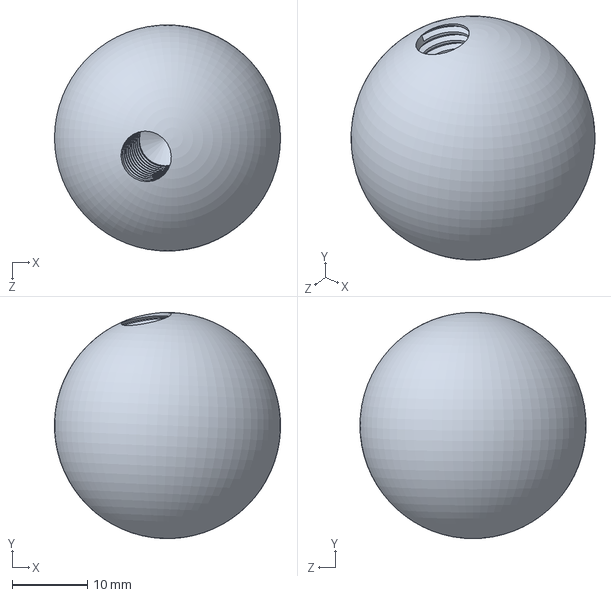
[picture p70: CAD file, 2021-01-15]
Modello/sfera_assemblaggio1.SLDPRT
30.0 x 30.0 x 30.0 mm

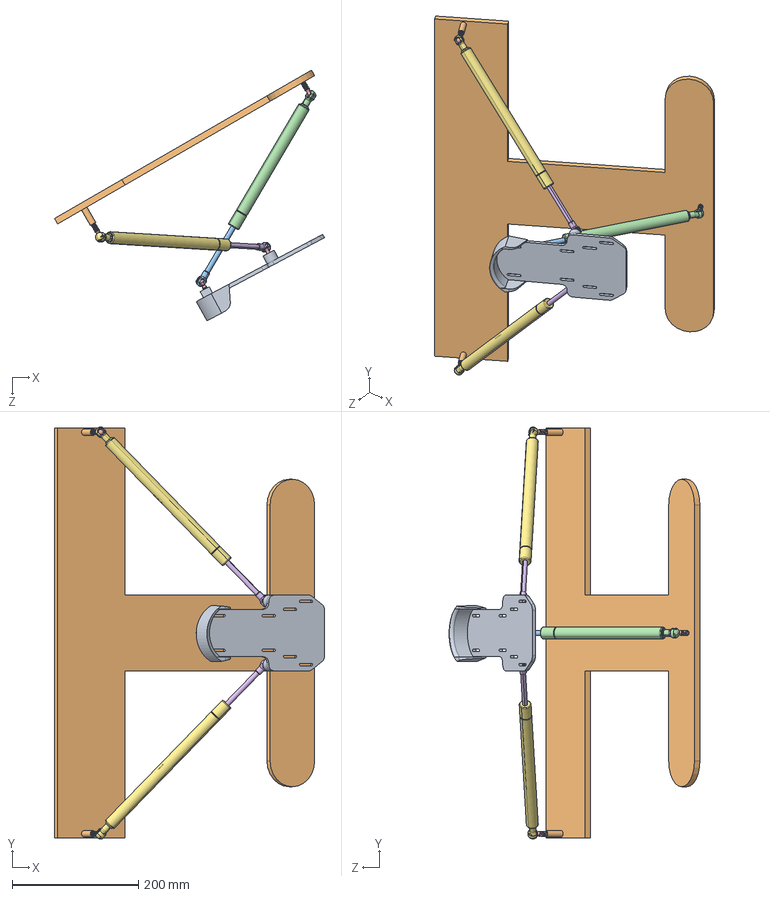
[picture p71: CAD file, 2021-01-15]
File extra/Bozza di lavoro/Assieme1_ver6.SLDASM
427.6 x 652.5 x 397.2 mm
pedana
Parte2
centrale_stelo
centrale_tubo
perno pistone centrale x 6
laterale_stelo x 2
laterale_tubo x 2

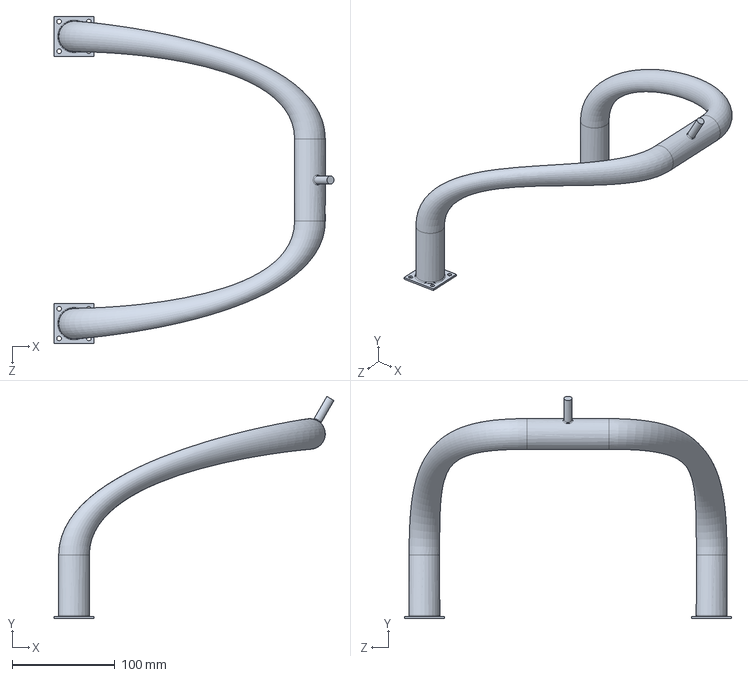
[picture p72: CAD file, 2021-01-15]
File extra/Simulazione 5/bsupp5_assemblaggio1.SLDPRT
273.0 x 216.6 x 319.0 mm

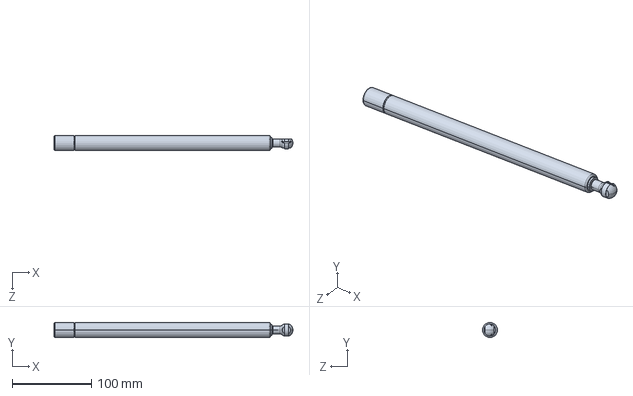
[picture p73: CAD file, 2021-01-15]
Modello/Pistoni/laterale_tubo_assemblaggio1.SLDPRT
301.7 x 19.0 x 19.0 mm

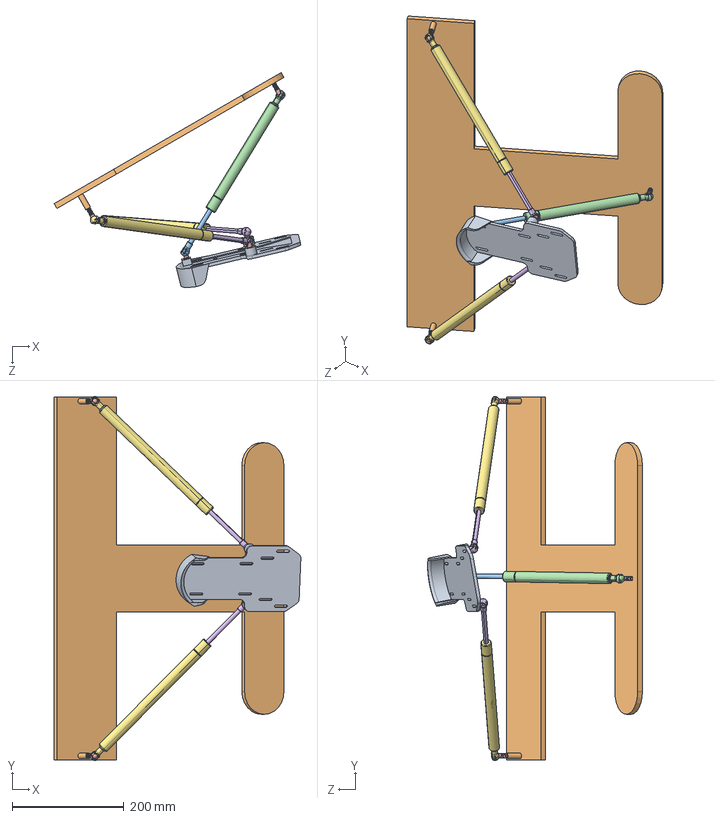
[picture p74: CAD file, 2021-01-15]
File extra/Bozza di lavoro/Assieme1_ver6 - Copia.SLDASM
442.3 x 652.5 x 385.2 mm
pedana
Parte2
centrale_stelo
centrale_tubo
perno pistone centrale x 6
laterale_stelo x 2
laterale_tubo x 2

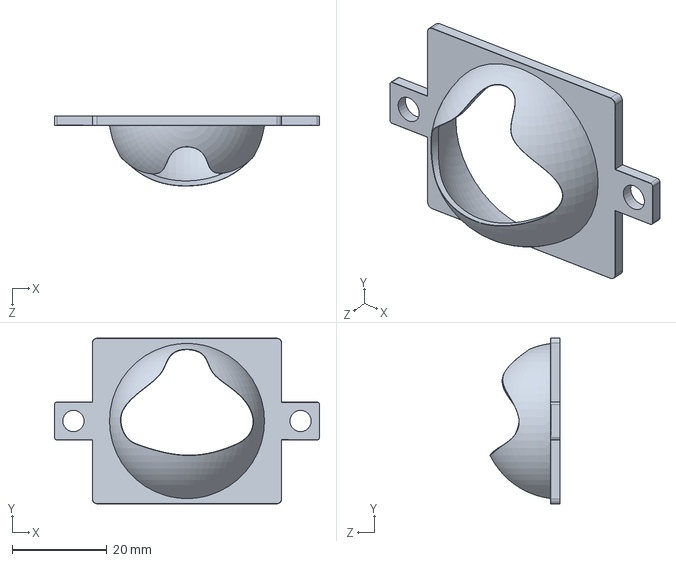
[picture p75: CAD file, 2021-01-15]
File extra/Simulazione 5/cappuccioAssieme_assemblaggio1.SLDPRT
56.0 x 35.0 x 14.8 mm

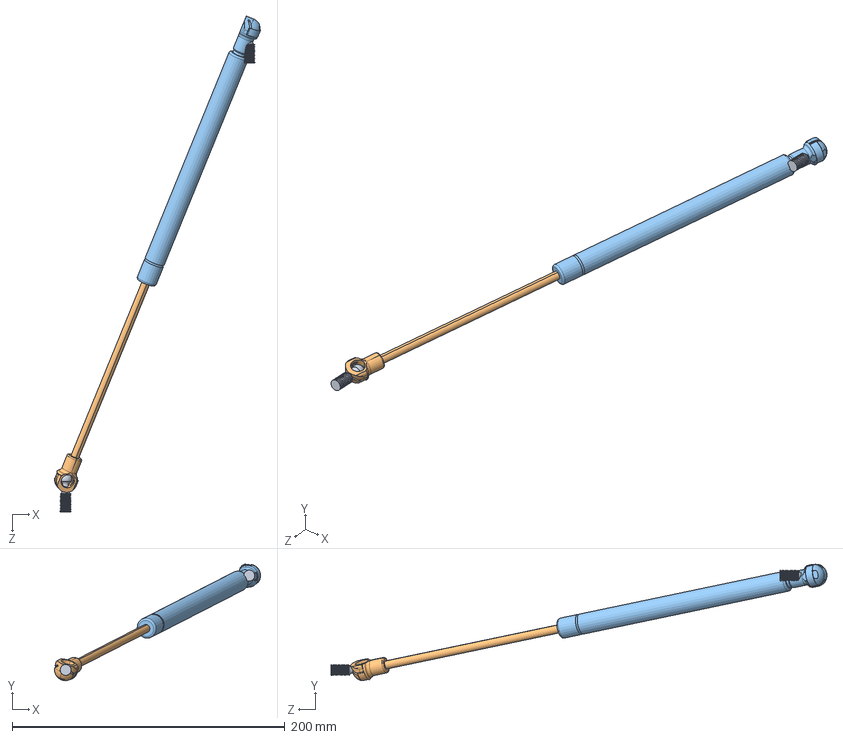
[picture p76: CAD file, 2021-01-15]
Modello/Pistoni/pistone centrale.SLDASM
151.1 x 85.5 x 363.7 mm
perno pistone centrale fino x 2
stelo
tubo

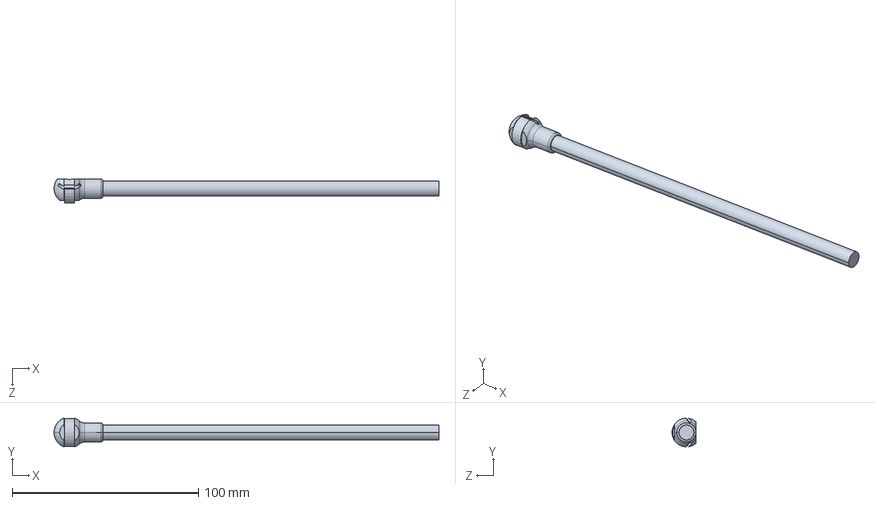
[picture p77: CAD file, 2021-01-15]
File extra/Simulazione 5/centrale_stelo_assemblaggio1.SLDPRT
206.7 x 15.5 x 13.0 mm

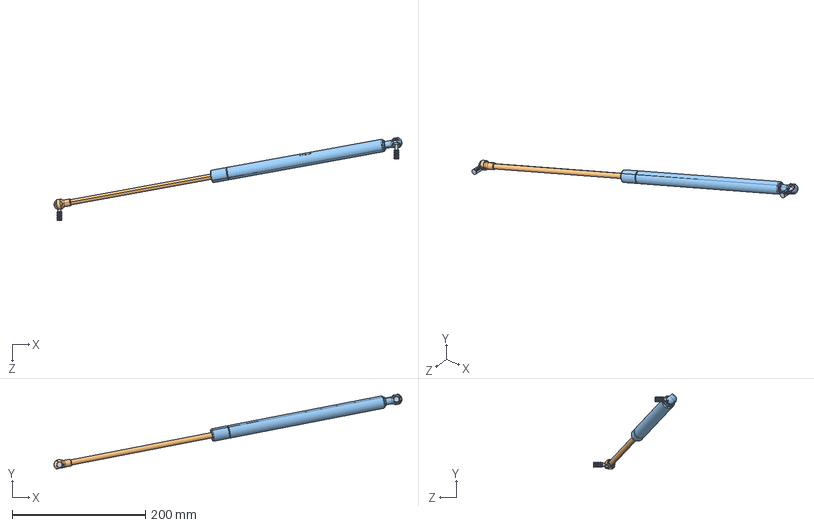
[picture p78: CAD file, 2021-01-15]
Modello/Pistoni/pistone laterale.SLDASM
522.3 x 112.6 x 124.5 mm
perno pistone centrale fino x 2
laterale_stelo_assemblaggio1
laterale_tubo_assemblaggio1

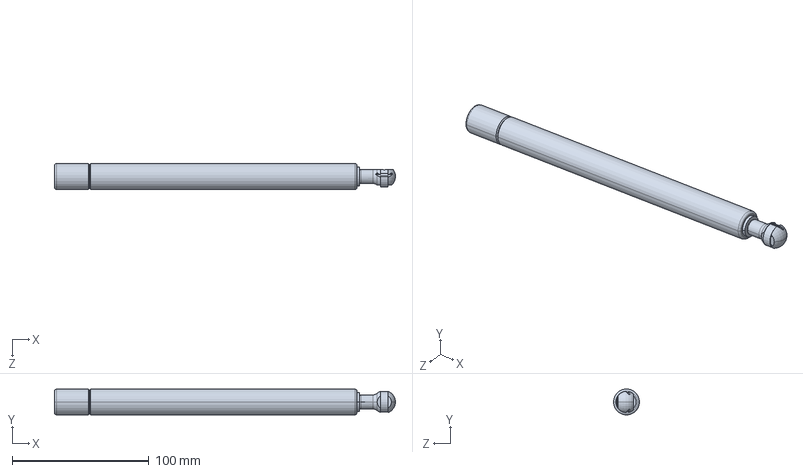
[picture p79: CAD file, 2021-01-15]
File extra/Simulazione 5/centrale_tubo_assemblaggio1.SLDPRT
249.7 x 18.9 x 19.0 mm

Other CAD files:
File extra/Simulazione 5/laterale_stelo_assemblaggio1.SLDPRT
File extra/Simulazione 5/laterale_tubo_assemblaggio1.SLDPRT
File extra/Simulazione 5/pedana2_assemblaggio1.SLDPRT
File extra/Simulazione 5/perno pistone centrale_assemblaggio1.SLDPRT
File extra/Bozza di lavoro/file corretto x misure_versione6.SLDPRT
File extra/Old/Pedana/Old/pedana.SLDDRW
File extra/Old/Pedana/Old/pedana.SLDPRT
File extra/Old/Pedana/pedana2.SLDDRW
File extra/Old/Pedana/pedana2.SLDPRT
File extra/Old/Pistoni/File di lavoro/LIFT-O-MAT® 2379SU_100N_K6_D6.SLDASM
File extra/Old/Pistoni/File di lavoro/LIFT-O-MAT® 9999RW_100N_K6_D6.SLDASM
File extra/Old/Pistoni/File di lavoro/centrale_stelo.SLDPRT
File extra/Old/Pistoni/File di lavoro/centrale_tubo.SLDPRT
File extra/Old/Pistoni/File di lavoro/laterale_stelo.SLDPRT
File extra/Old/Pistoni/File di lavoro/laterale_tubo _lungo.SLDPRT
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

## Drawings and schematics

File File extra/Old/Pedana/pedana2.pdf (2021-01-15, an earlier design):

E | E
F | F

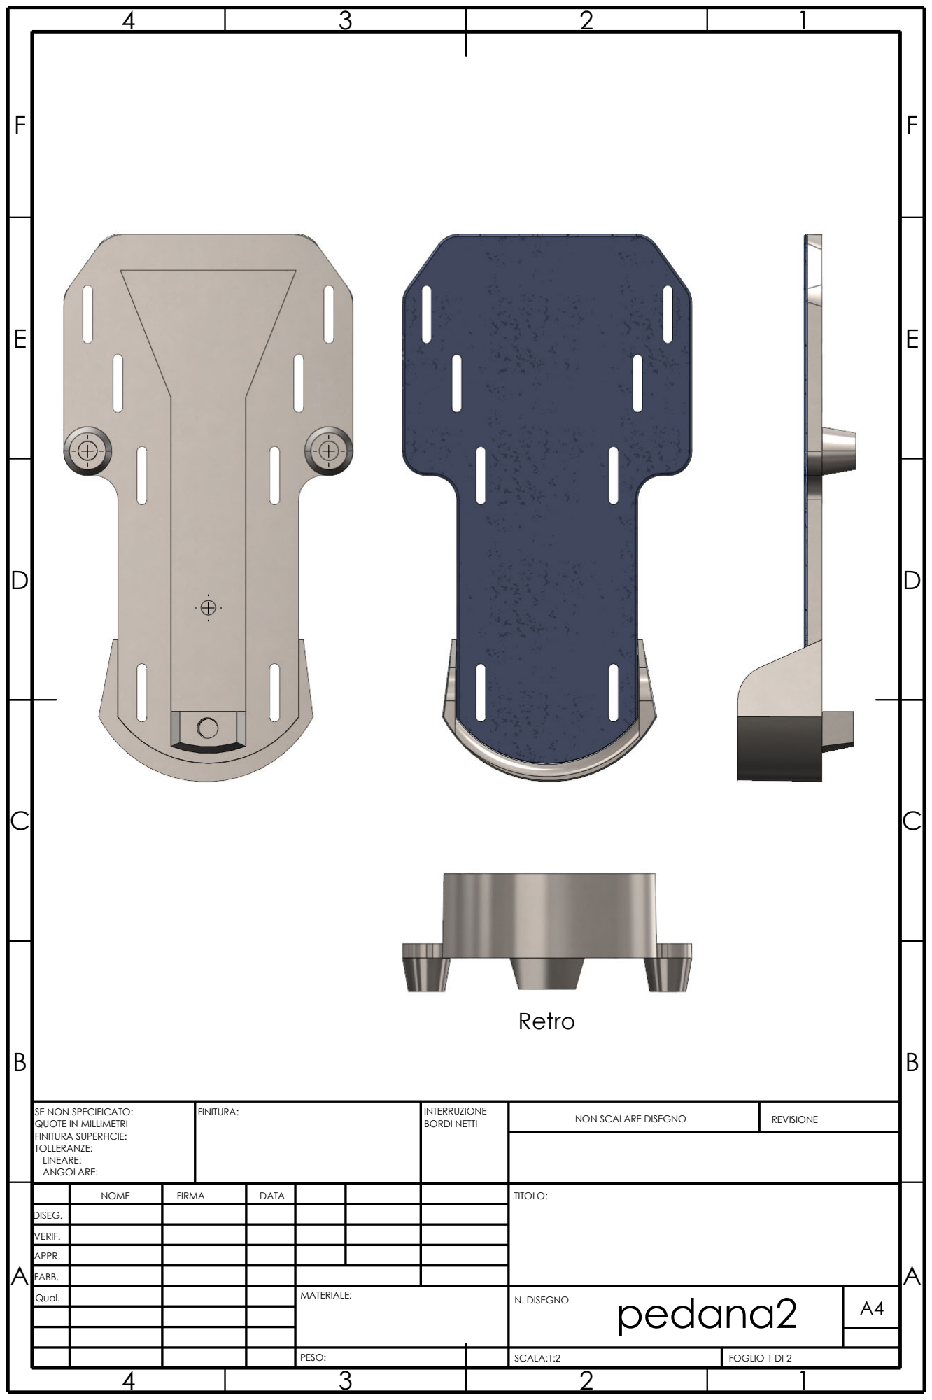
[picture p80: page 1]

A | A
B | | B
| NOME | FIRMA | DATA | | | | TITOLO:
DISEG.
VERIF.
APPR.

FABB.
Qual. | | | | MATERIALE: | pedana2 N. DISEGNO | A4
C | C
D | D

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
SE NON SPECIFICATO:
QUOTE IN MILLIMETRI
FINITURA SUPERFICIE:
TOLLERANZE:
LINEARE:
ANGOLARE:
FINITURA: | INTERRUZIONE
BORDI NETTI
NON SCALARE DISEGNO | REVISIONE
SCALA:1:2 | FOGLIO 1 DI 2

PESO:

# Retro

E | E
F | F

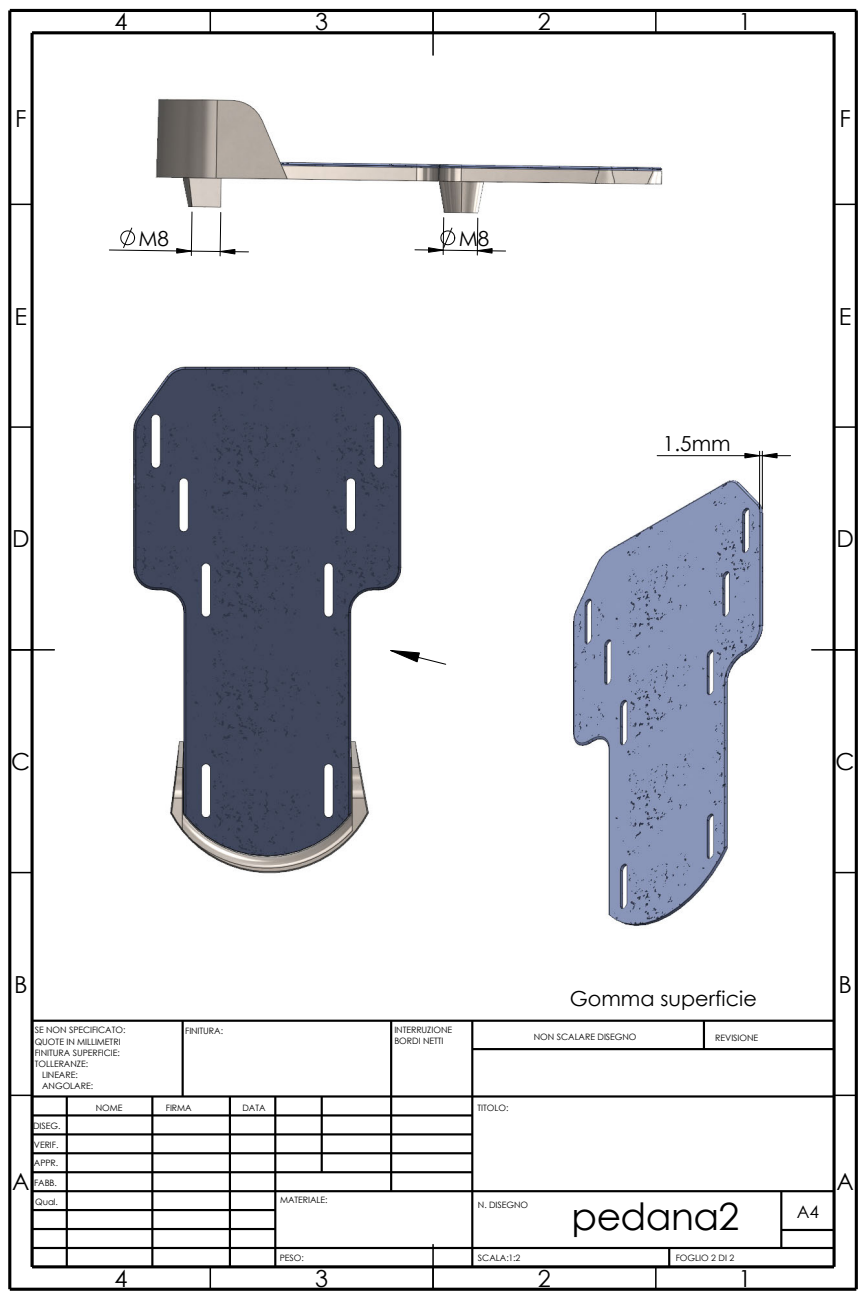
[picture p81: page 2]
FINITURA:; INTERRUZIONE; BORDI NETTI; NON SCALARE DISEGNO; REVISIONE; SCALA:1:2; FOGLIO 2 DI 2; PESO:; Gomma superficie

SE NON SPECIFICATO:
QUOTE IN MILLIMETRI
FINITURA SUPERFICIE:
TOLLERANZE:
LINEARE:
ANGOLARE:

NOME | FIRMA | DATA | | | | TITOLO:

DISEG.
VERIF.
APPR.
FABB.
Qual. | | | | MATERIALE: | pedana2 N. DISEGNO | A4

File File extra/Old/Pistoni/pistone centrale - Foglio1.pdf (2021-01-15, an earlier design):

E | E
F | F

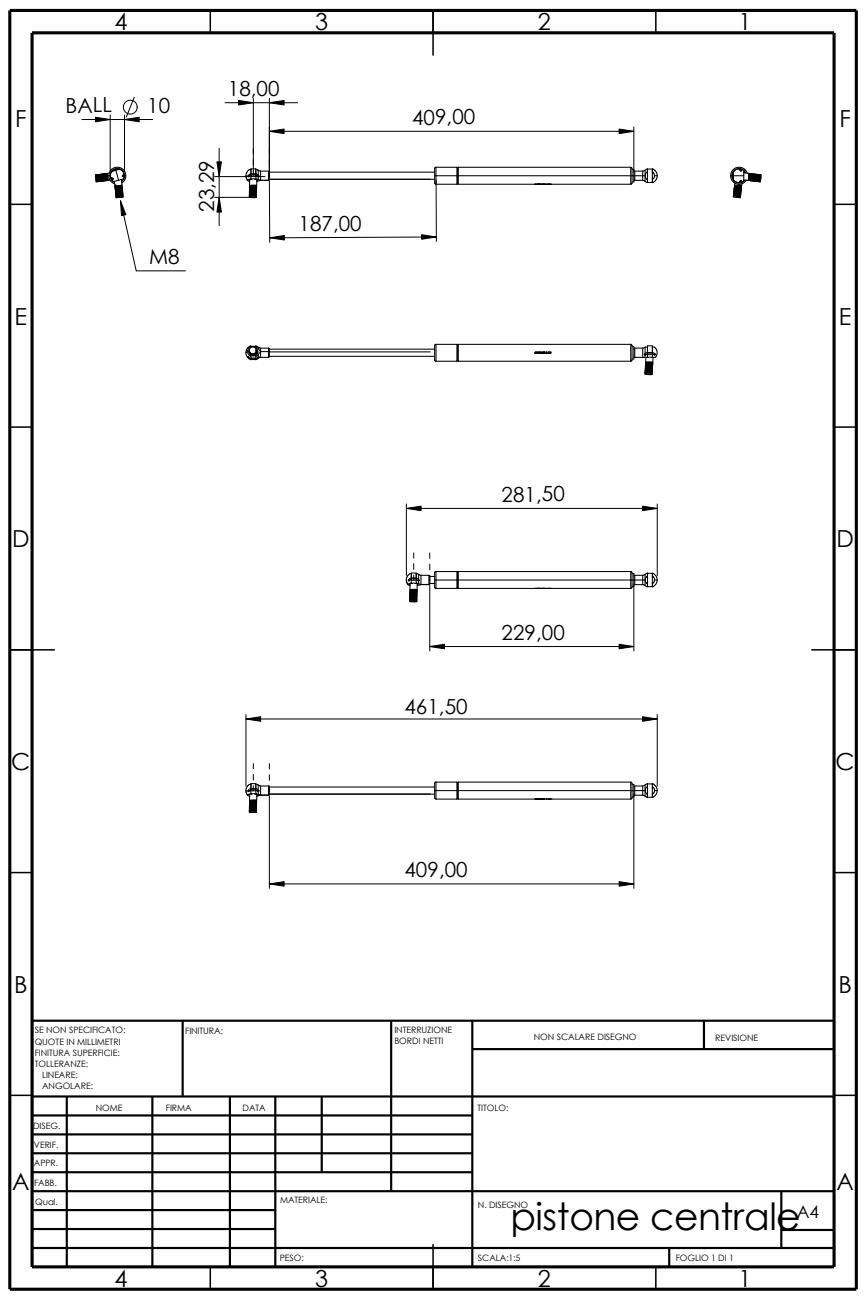
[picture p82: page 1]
SCALA:1:5; PESO:; FOGLIO 1 DI 1; NON SCALARE DISEGNO; REVISIONE; FINITURA:; BORDI NETTI; INTERRUZIONE; BALL

SE NON SPECIFICATO:
QUOTE IN MILLIMETRI
FINITURA SUPERFICIE:
TOLLERANZE:
LINEARE:
ANGOLARE:

NOME | FIRMA | DATA | | | | TITOLO:

DISEG.
VERIF.
APPR.
FABB.
Qual. | | | | MATERIALE: | pistone centrale N. DISEGNO | A4

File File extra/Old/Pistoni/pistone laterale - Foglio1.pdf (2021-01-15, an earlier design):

E | E
F | F

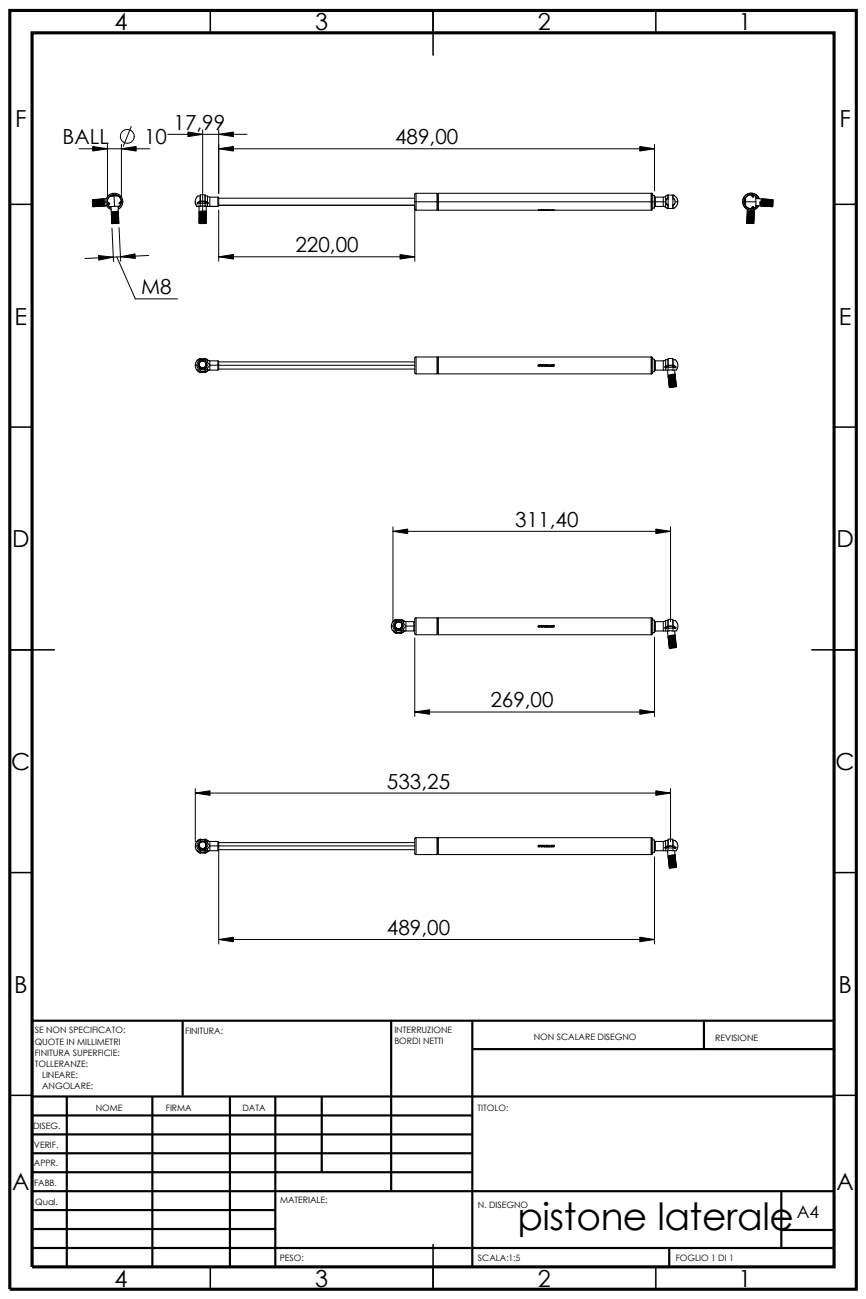
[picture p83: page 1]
PESO:; SCALA:1:5; FOGLIO 1 DI 1; TITOLO:; REVISIONE; N. DISEGNO; MATERIALE:; FINITURA:; BORDI NETTI; NOME; FIRMA; DATA; INTERRUZIONE; pistone laterale; BALL

SE NON SPECIFICATO:
QUOTE IN MILLIMETRI
FINITURA SUPERFICIE:
TOLLERANZE:
LINEARE:
ANGOLARE:

NON SCALARE DISEGNO

DISEG.
VERIF.
APPR.
FABB. Qual.

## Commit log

2021-01-15 Create Assieme1_ver6 - Copia.SLDASM
    [Assieme1_ver6 - Copia.SLDASM]
2021-01-15 Create file corretto x misure_versione6.SLDPRT
    [file corretto x misure_versione6.SLDPRT]
2021-01-15 Create pistone laterale.SLDASM
    [pistone laterale.SLDASM]
2021-01-15 Create pistone centrale.SLDASM
    [pistone centrale.SLDASM]
2021-01-15 Create perno pistone centrale fino.SLDPRT
    [perno pistone centrale fino.SLDPRT]
2021-01-15 Create pistone laterale_assemblaggio1.SLDASM
    [pistone laterale_assemblaggio1.SLDASM]
2021-01-15 Create pistone laterale_assemblaggio1 (Copia in conflitto di Alessandro Mastrofini 2021-01-14).SLDASM
    [pistone laterale_assemblaggio1 (Copia in conflitto di Alessandro Mastrofini 2021-01-14).SLDASM]
2021-01-15 Create pistone centrale_assemblaggio1.SLDASM
    [pistone centrale_assemblaggio1.SLDASM]
2021-01-15 Create pistone centrale_assemblaggio1 (Copia in conflitto di Alessandro Mastrofini 2021-01-14).SLDASM
    [pistone centrale_assemblaggio1 (Copia in conflitto di Alessandro Mastrofini 2021-01-14).SLDASM]
2021-01-15 Create perno pistone laterale.SLDPRT
    [perno pistone laterale.SLDPRT]
2021-01-15 Create perno pistone centrale_assemblaggio1.SLDPRT
    [perno pistone centrale_assemblaggio1.SLDPRT]
2021-01-15 Create bsupp6 - Copia.SLDPRT
    [bsupp6 - Copia.SLDPRT]
2021-01-15 Create pistone laterale.SLDDRW
    [pistone laterale.SLDDRW]
2021-01-15 Create pistone centrale.SLDDRW
    [pistone centrale.SLDDRW]
2021-01-15 Create perno pistone centrale.SLDPRT
    [perno pistone centrale.SLDPRT]
2021-01-15 Create LIFT-O-MAT® 9999RW_100N_K6_D6.SLDASM
    [LIFT-O-MAT® 9999RW_100N_K6_D6.SLDASM]
2021-01-15 Create LIFT-O-MAT® 2379SU_100N_K6_D6.SLDASM
    [LIFT-O-MAT® 2379SU_100N_K6_D6.SLDASM]
2021-01-15 Create laterale_tubo _lungo.SLDPRT
    [laterale_tubo _lungo.SLDPRT]
2021-01-15 Create flexdorsìrot yaw.csv
    [flexdorsìrot yaw.csv]
2021-01-15 Create flexdorsìrot roll.csv
    [flexdorsìrot roll.csv]
2021-01-15 Create flexdorsìrot pitch.csv
    [flexdorsìrot pitch.csv]
2021-01-15 Create flex+rot yaw.csv
    [flex+rot yaw.csv]
2021-01-15 Create flex+rot roll.csv
    [flex+rot roll.csv]
2021-01-15 Create flex+rot pitch.csv
    [flex+rot pitch.csv]
2021-01-15 Create flex dorsale + pitch.xlsx
    [flex dorsale + pitch.xlsx]
2021-01-15 Create coppia rotazione.csv
    [coppia rotazione.csv]
2021-01-15 Create coppia roll.csv
    [coppia roll.csv]
2021-01-15 Create coppia flessione plantare.csv
    [coppia flessione plantare.csv]
2021-01-15 Create coppia flessione dorsale.csv
    [coppia flessione dorsale.csv]
